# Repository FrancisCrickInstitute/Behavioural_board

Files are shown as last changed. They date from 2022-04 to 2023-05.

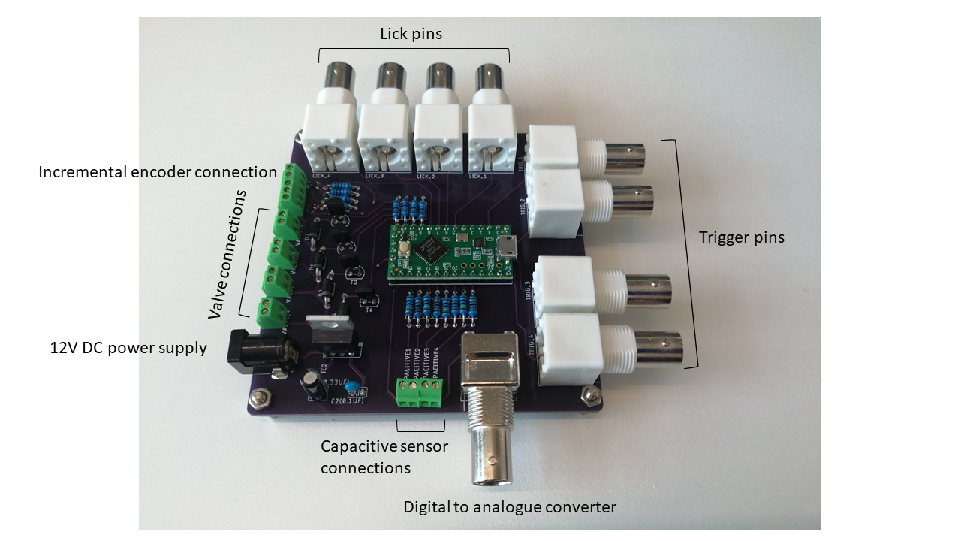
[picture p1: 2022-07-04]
Behavioural board V2.png

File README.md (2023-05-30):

# Behavioural_board

This piece of hardware is a Teensy 3.2, Teensy LC or Teensy 4 [1] breakout board with 4 valve controls and (capacitive) licking sensors and with the same amount of digital inputs/outputs (8 in total). This device pretends to be a tool for behavioural experiments which need to control up to four valves and sense 4 licking sensors. The board has eight digital pins with interrupt capability. These pins are connected to a BNC and they can be used to display digital signals or to trigger externally the valves for instance. The Teensy 3.2 performs very well on the capacitive sensor library [2] achieving sub-millisecond sampling periods while using one licking sensor at 120 MHz clock speed. All thought the licking frequency in mice is ~7 Hz, sub-millisecond resolution is required when accurate sensing of lick onset and offset is desired [3]. There is also an Incremental encoder connection for 5V Encoders with logic level shifters for phases A and B.

Behavioural board v2

# R1-R8 resistor values (Capacitive sensor pins resistors)
The value of the capacitive sensor emitter is 1MΩ and the receiver digital pin has a 1kΩ resistance value to avoid an accidental electric shock [5]. The value of the high resistance value resistor can be changed to higher values in order to increase sensitivity.

# R9-R12 Calculation example (Transistor base current)
The solenoid valve used for the design is the Lee company model LHDA0533215H. The current needed on the transistor collector has been calculated using the power and the resistance from the manufacturer specifications [4]. Different solenoid valves may require changing the transistor base resistor. More details on "R9-R12 Calculation example (Transistor base).pdf"

# Limitations

If you are using Teensy LC Pin 1 does not have interrupt capability, therefore Trigger 1 cannot be used using interrupts. The DAC BNC connector is wired with to A14 of Teensy 3.2  and A12 of LC so it cannot be used with the Teensy 4.0.

# References

[1] 	"https://www.pjrc.com/teensy/teensy31.html". 

[2] 	"https://github.com/PaulStoffregen/CapacitiveSensor". 

[3] 	B. Williams, A. Speed and B. Haider, "A novel device for real-time measurement and manipulation of licking behavior in head-fixed mice," Journal of Neurophisiology, vol. 120, pp. 2975-2987, 2018. 

[4] 	"https://www.theleeco.com/products/electro-fluidic-systems/solenoid-valves/control-valves/lhd-series/3-port/ported/". 

[5] 	"https://www.pjrc.com/teensy/td_libs_CapacitiveSensor.html".

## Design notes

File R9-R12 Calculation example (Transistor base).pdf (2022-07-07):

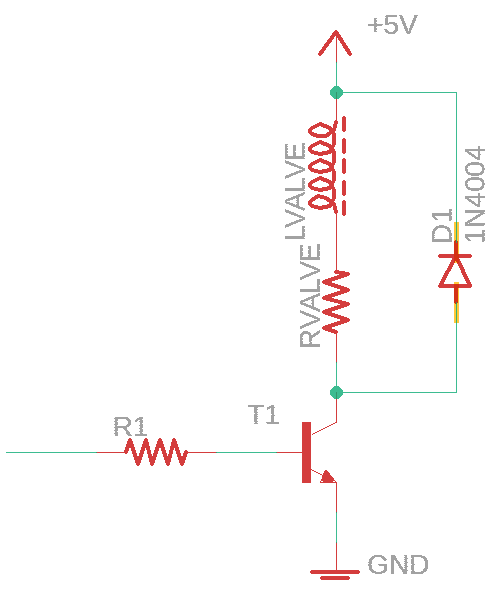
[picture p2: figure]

Pvalve = 550 mW Rvalve = 46 Ω

Pvalve = Ivalve

2
∗ Rvalve

Ivalve = √
Pvalve

Rvalve

= √
550 mW
46 Ω

Ivalve = 109 mA

BC 337 NPN Transistor

ℎFE = 100 IC = 100mA VCE(ON) = 1.2V

IB =

IC

ℎFE

=

100 mA
100 = 1mA

BE mesh

−TTL + IBR + VCE(ON) = 0

−3.3V + (1 mA)R + 1.2V = 0

R1 =

2.1V
1mA = 2.1kΩ

CE mesh

−Vcc + RvalveIC + VCE = 0

−3.3V + 46Ω 100mA + VCE = 0

VCE = 1.3V

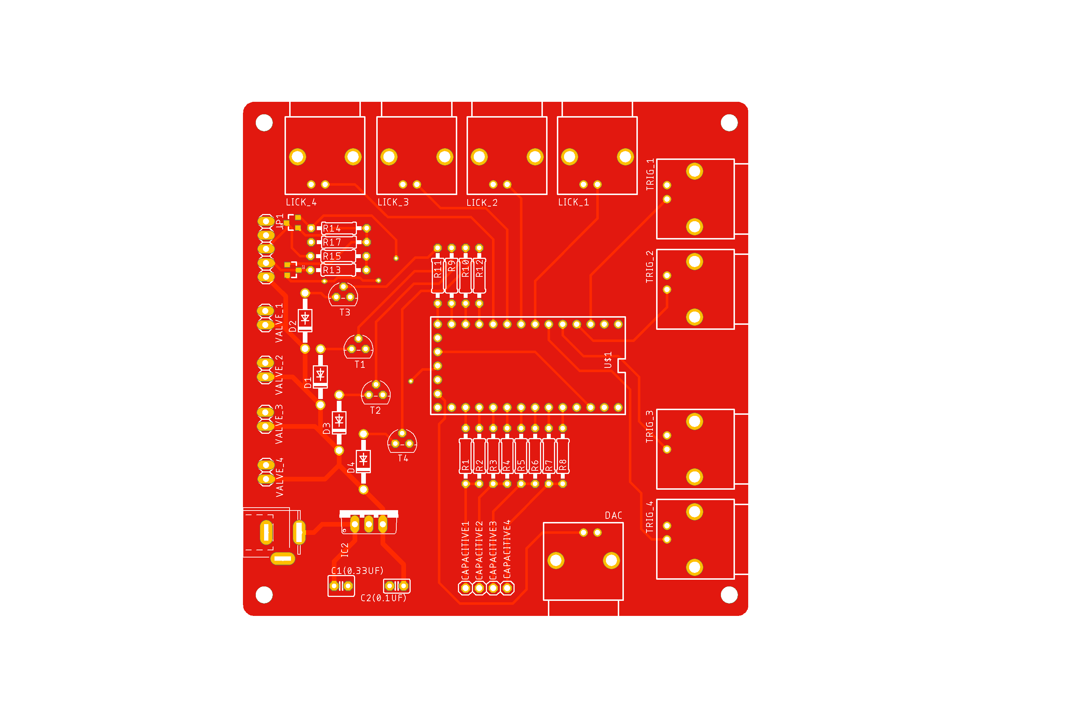
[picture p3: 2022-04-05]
Design files/Behavioural board V2.png

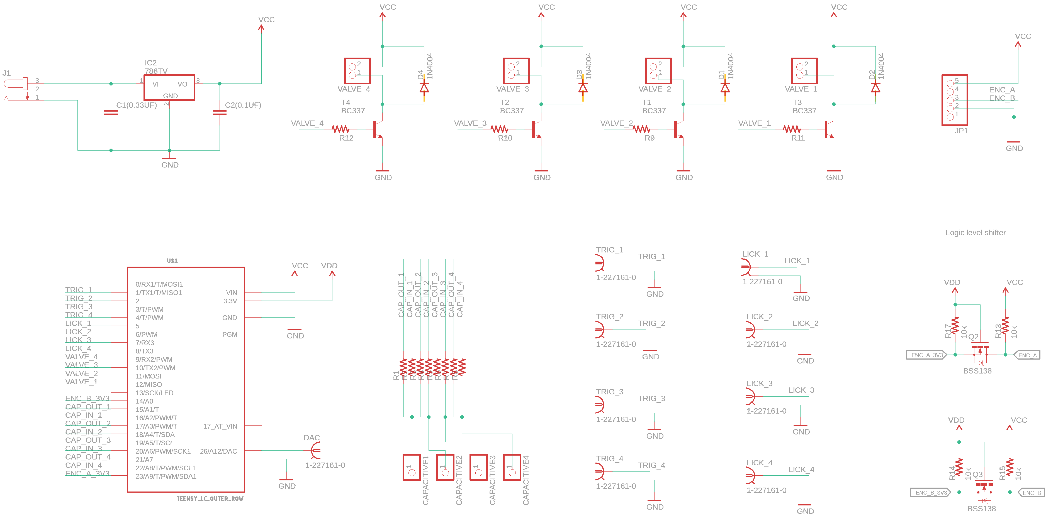
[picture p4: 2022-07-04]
Design files/Behavioural board V2 Schematic.png

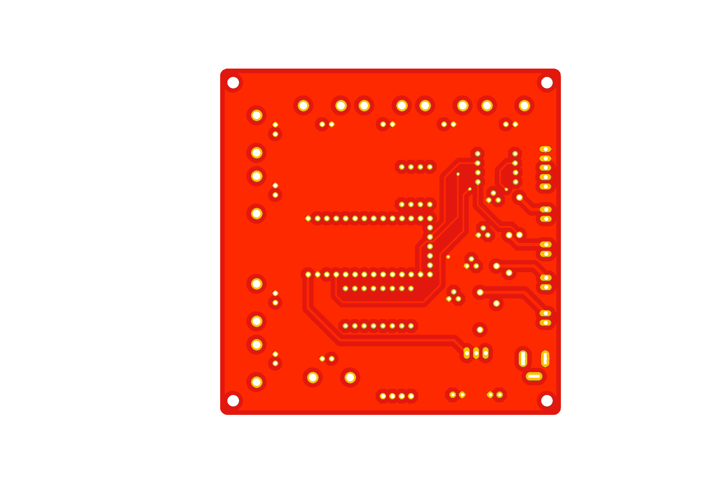
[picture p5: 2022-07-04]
Design files/Behavioural board V2 bottom.png

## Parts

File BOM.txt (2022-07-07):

Partlist exported from C:/Users/ferrerx/Documents/GitHub/Behavioural_board/Design files/Behavioural board V2.sch at 6/17/2022 1:58 PM

Qty Value               Device              Package                     Parts                                                               Description                            MF               MPN      OC_FARNELL OC_NEWARK POPULARITY SPICEPREFIX
1                       C2.5/2              C2.5-2                      C2(0.1UF)                                                           CAPACITOR                                                                             28                    
1                       C2.5/4              C2.5-4                      C1(0.33UF)                                                          CAPACITOR                                                                             6                     
1                       JACK-PLUG0          SPC4077                     J1                                                                  DC POWER JACK                                                    unknown    unknown   0                     
4                       PINHD-1X1           1X01                        CAPACITIVE1, CAPACITIVE2, CAPACITIVE3, CAPACITIVE4                  PIN HEADER                                                                            64                    
4                       PINHD-1X2           1X02                        VALVE_1, VALVE_2, VALVE_3, VALVE_4                                  PIN HEADER                                                                            98                    
1                       PINHD-1X5           1X05                        JP1                                                                 PIN HEADER                                                                            69                    
12                      R-US_0207/10        0207/10                     R1, R2, R3, R4, R5, R6, R7, R8, R9, R10, R11, R12                   RESISTOR, American symbol                                                             36         R          
9   1-227161-0          1-227161-0          AMP_227161                  DAC, LICK_1, LICK_2, LICK_3, LICK_4, TRIG_1, TRIG_2, TRIG_3, TRIG_4 JACK,  RIGHT ANGLE, 50 OHM, PCB, BNC   TYCO ELECTRONICS 1-227161 unknown    33B3200   0                     
4   10k                 R-US_0207/10        0207/10                     R13, R14, R15, R17                                                  RESISTOR, American symbol                                                             36         R          
4   1N4004              1N4004              DO41-10                     D1, D2, D3, D4                                                      DIODE                                                                                 82                    
1   786TV               786TV               TO220V                      IC2                                                                 Positive VOLTAGE REGULATOR                                                            0                     
4   BC337               BC337               TO92                        T1, T2, T3, T4                                                      NPN TRANSISTOR                                                                        2                     
2   BSS138              MOSFET-NCHANNELSMD  SOT23-3                     Q2, Q3                                                                                                                                                                          
1   TEENSY_LC_OUTER_ROW TEENSY_LC_OUTER_ROW TEENSY_3.0-3.2&LC_OUTER_ROW U$1                                                                 Teensy LC with only outer row of pins.

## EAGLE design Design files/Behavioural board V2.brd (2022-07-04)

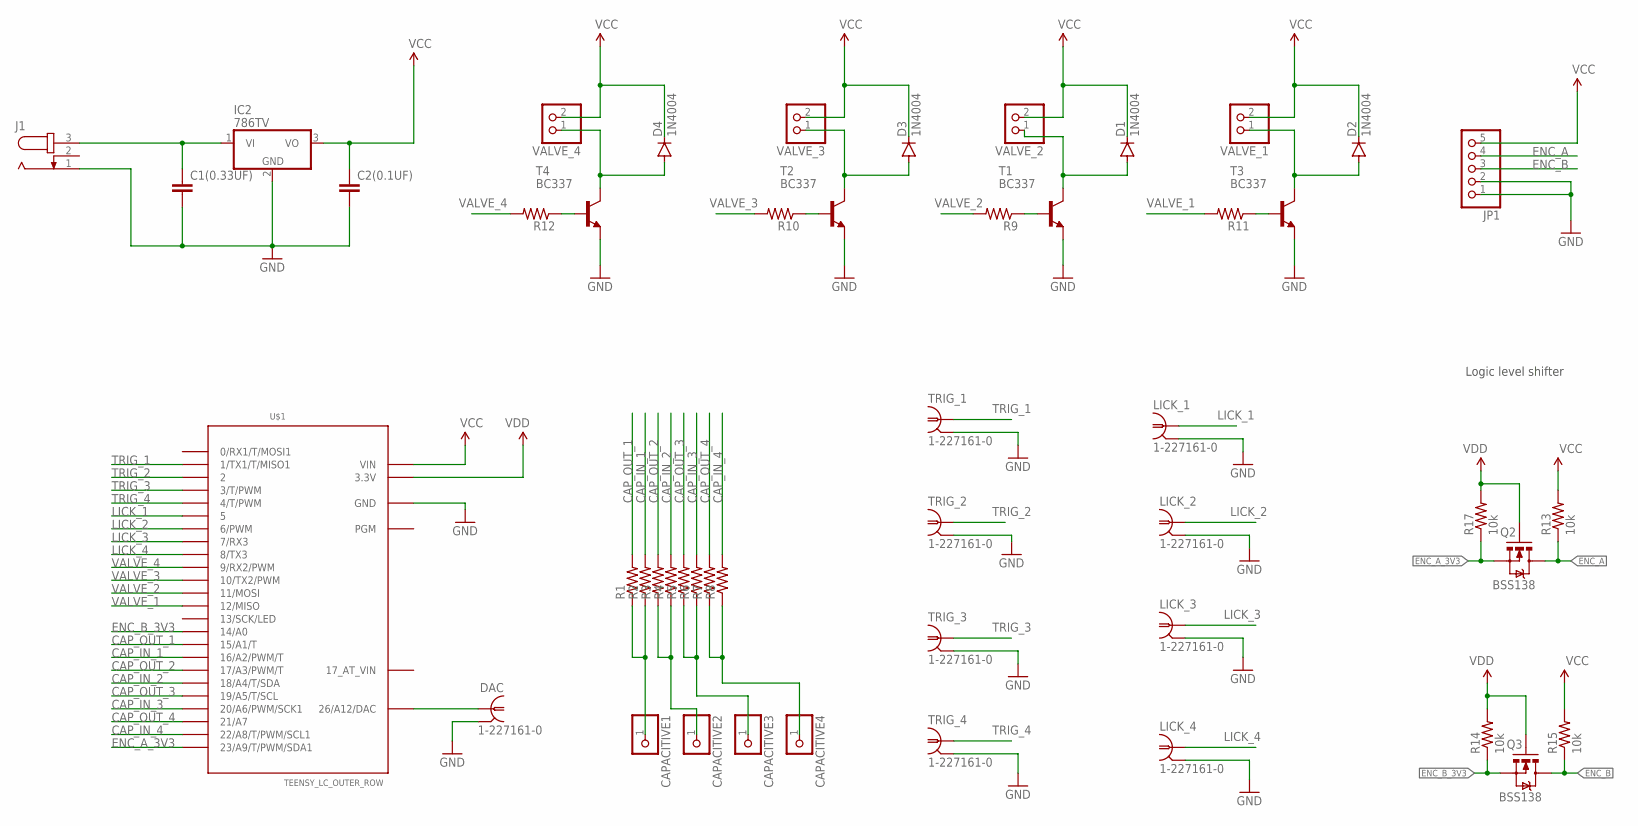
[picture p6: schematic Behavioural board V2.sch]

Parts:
C1(0.33UF): C2.5/4; C2.5-4
C2(0.1UF): C2.5/2; C2.5-2
CAPACITIVE1, CAPACITIVE2, CAPACITIVE3, CAPACITIVE4: PINHD-1X1; 1X01
D1, D2, D3, D4: 1N4004; DO41-10
DAC: 1-227161-0; AMP_227161
IC2: 786TV; TO220V
J1: JACK-PLUG0; SPC4077
JP1: PINHD-1X5; 1X05
LICK_1, LICK_2, LICK_3, LICK_4: 1-227161-0; AMP_227161
Q2, Q3: BSS138; SOT23-3
R1, R2, R3, R4, R5, R6, R7, R8, R9, R10, R11, R12: R-US_0207/10; 0207/10
R13, R14, R15, R17: 10k; 0207/10
T1, T2, T3, T4: BC337; TO92
TRIG_1, TRIG_2, TRIG_3, TRIG_4: 1-227161-0; AMP_227161
U$1: TEENSY_LC_OUTER_ROW; TEENSY_3.0-3.2&LC_OUTER_ROW
VALVE_1, VALVE_2, VALVE_3, VALVE_4: PINHD-1X2; 1X02

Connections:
12V: C1(0.33UF).1, IC2.1 (VI), J1.3
CAP_IN_1: R2.2, U$1.16/A2 (16/A2/PWM/T)
CAP_IN_2: R4.2, U$1.18/A4 (18/A4/T/SDA)
CAP_IN_3: R6.2, U$1.20/A6 (20/A6/PWM/SCK1)
CAP_IN_4: R8.2, U$1.22/A8 (22/A8/T/PWM/SCL1)
CAP_OUT_1: R1.2, U$1.15/A1 (15/A1/T)
CAP_OUT_2: R3.2, U$1.17/A3 (17/A3/PWM/T)
CAP_OUT_3: R5.2, U$1.19/A5 (19/A5/T/SCL)
CAP_OUT_4: R7.2, U$1.21/A7
ENC_A: JP1.4, Q2.3 (D), R13.1
ENC_A_3V3: Q2.2 (S), R17.1, U$1.23/A9 (23/A9/T/PWM/SDA1)
ENC_B: JP1.3, Q3.3 (D), R15.1
ENC_B_3V3: Q3.2 (S), R14.1, U$1.14/A0
GND: C1(0.33UF).2, C2(0.1UF).2, DAC.2, IC2.2 (GND), J1.1, JP1.1, JP1.2, LICK_1.2, LICK_2.2, LICK_3.2, LICK_4.2, T1.1 (E), T2.1 (E), T3.1 (E), T4.1 (E), TRIG_1.2, TRIG_2.2, TRIG_3.2, TRIG_4.2, U$1.AGND (GND), U$1.GND, U$1.GND1 (GND)
LICK_1: LICK_1.1, U$1.5
LICK_2: LICK_2.1, U$1.6 (6/PWM)
LICK_3: LICK_3.1, U$1.7 (7/RX3)
LICK_4: LICK_4.1, U$1.8 (8/TX3)
unnamed: DAC.1, U$1.RESET/DAC (26/A12/DAC)
unnamed: CAPACITIVE1.1, R1.1, R2.1
unnamed: CAPACITIVE2.1, R3.1, R4.1
unnamed: CAPACITIVE3.1, R5.1, R6.1
unnamed: CAPACITIVE4.1, R7.1, R8.1
unnamed: R11.1, T3.2 (B)
unnamed: D2.A, T3.3 (C), VALVE_1.1
unnamed: R9.1, T1.2 (B)
unnamed: D1.A, T1.3 (C), VALVE_2.1
unnamed: R10.1, T2.2 (B)
unnamed: D3.A, T2.3 (C), VALVE_3.1
unnamed: R12.1, T4.2 (B)
unnamed: D4.A, T4.3 (C), VALVE_4.1
TRIG_1: TRIG_1.1, U$1.1 (1/TX1/T/MISO1)
TRIG_2: TRIG_2.1, U$1.2
TRIG_3: TRIG_3.1, U$1.3 (3/T/PWM)
TRIG_4: TRIG_4.1, U$1.4 (4/T/PWM)
VALVE_1: R11.2, U$1.12 (12/MISO)
VALVE_2: R9.2, U$1.11 (11/MOSI)
VALVE_3: R10.2, U$1.10 (10/TX2/PWM)
VALVE_4: R12.2, U$1.9 (9/RX2/PWM)
VCC: C2(0.1UF).1, D1.C, D2.C, D3.C, D4.C, IC2.3 (VO), JP1.5, R13.2, R15.2, U$1.VIN, VALVE_1.2, VALVE_2.2, VALVE_3.2, VALVE_4.2
VDD: Q2.1 (G), Q3.1 (G), R14.2, R17.2, U$1.3.3V, U$1.3.3V1 (3.3V)

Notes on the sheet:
Logic level shifter

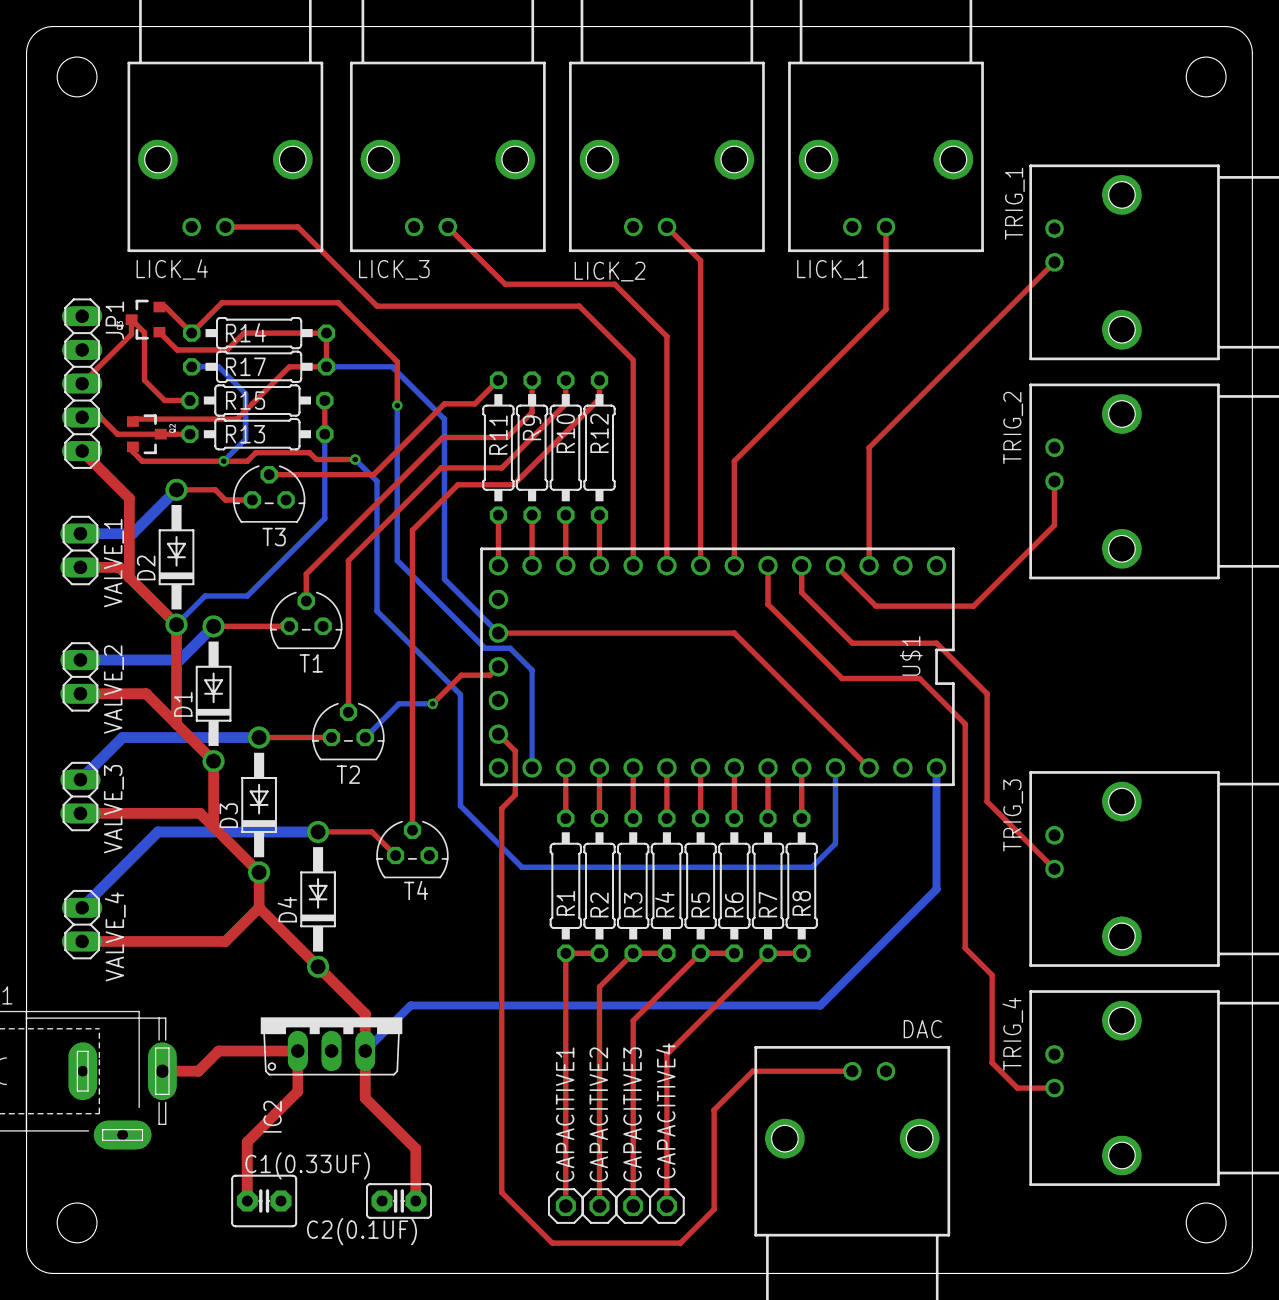
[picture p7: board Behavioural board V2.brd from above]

Board: 2 copper layers, 92.4 x 94.0 mm, 49 parts (0 on the bottom side), 41 nets.

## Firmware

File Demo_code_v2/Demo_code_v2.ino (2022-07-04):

#include <CapacitiveSensor.h>

byte N = 20;

//Capacitive sensor objects
CapacitiveSensor   CS_1 = CapacitiveSensor(15,16);
CapacitiveSensor   CS_2 = CapacitiveSensor(17,18);
CapacitiveSensor   CS_3 = CapacitiveSensor(19,20);
CapacitiveSensor   CS_4 = CapacitiveSensor(21,22);

// Licking sensor variables
long lick_1;
long lick_2;
long lick_3;
long lick_4;

//Valve variables
int valve_1 = 12;
int valve_2 = 11;
int valve_3 = 10;
int valve_4 = 9;

//Input/output pins

int trig_1 = 1; //IO_pin_1
int trig_2 = 2; //IO_pin_2
int trig_3 = 3; //IO_pin_3
int trig_4 = 4; //IO_pin_4
int lick_1_out = 5; //IO_pin_5
int lick_2_out = 6; //IO_pin_6
int lick_3_out = 7; //IO_pin_7
int lick_4_out = 8; //IO_pin_8

volatile bool state = LOW;
volatile bool state_2 = LOW;
volatile bool state_3 = LOW;
volatile bool state_4 = LOW;

elapsedMillis outputTimer = 0;

int th = 5000;

//Encoder encoder(23,14); // mistake connecting encoder to pin 13 (it has the LED attached)

void setup() 
{
  CS_1.set_CS_AutocaL_Millis(0xFFFFFFFF);
  CS_2.set_CS_AutocaL_Millis(0xFFFFFFFF);
  CS_3.set_CS_AutocaL_Millis(0xFFFFFFFF);
  CS_4.set_CS_AutocaL_Millis(0xFFFFFFFF);

  //Pins to be externally triggered
  //pinMode(trig_1, INPUT_PULLUP); // Teensy LC does not have interrupt capability on pin 1
  pinMode(trig_2, INPUT_PULLUP);
  pinMode(trig_3, INPUT_PULLUP);
  pinMode(trig_4, INPUT_PULLUP);
  
  //Interrupt routines can be used to externally trigger the valves for instance
  //attachInterrupt(digitalPinToInterrupt(trig_1),change, RISING); // Teensy LC does not have interrupt capability on pin 1
  attachInterrupt(digitalPinToInterrupt(trig_2),change_2, RISING);
  attachInterrupt(digitalPinToInterrupt(trig_3),change_3, RISING);
  attachInterrupt(digitalPinToInterrupt(trig_4),change_4, RISING);
  
  // Pins that can be used as a digital oputput
//  pinMode(trig_1, OUTPUT);
//  pinMode(trig_2, OUTPUT);
//  pinMode(trig_3, OUTPUT);
//  pinMode(trig_4, OUTPUT);

  //Valve pins declared as an output
  pinMode(lick_1_out, OUTPUT);
  pinMode(lick_2_out, OUTPUT);
  pinMode(lick_3_out, OUTPUT);
  pinMode(lick_4_out, OUTPUT);

  // Pins that can be used as a digital oputput
  digitalWrite(lick_1_out, LOW);
  digitalWrite(lick_2_out, LOW);
  digitalWrite(lick_3_out, LOW);
  digitalWrite(lick_4_out, LOW);

  //Valve pins declared as an output
  pinMode(valve_1, OUTPUT);
  pinMode(valve_2, OUTPUT);
  pinMode(valve_3, OUTPUT);
  pinMode(valve_4, OUTPUT);
}

void loop() 
{
  //Variable to check the performance of the loop function in us
  //long start = micros();

  //Read all the licking sensors
  lick_1 =  CS_1.capacitiveSensor(N);
  lick_2 =  CS_2.capacitiveSensor(N);
  lick_3 =  CS_3.capacitiveSensor(N);
  lick_4 =  CS_4.capacitiveSensor(N);

  // Actuate the valves, when each of the trig_ pins see a rising edge the state variable changes cand the 
  // vale state also changes
  //digitalWrite(valve_1,state);
  digitalWrite(valve_2,state_2);
  digitalWrite(valve_3,state_3);
  digitalWrite(valve_4,state_4);

  // Convert the licking signal to a digital output for a certain threshold
  if (lick_1 >= th)
    {
      digitalWrite(lick_1_out, HIGH);
    }
  else if (lick_1 < th)
    {
      digitalWrite(lick_1_out, LOW);
    }
    
  if (lick_2 >= th)
    {
      digitalWrite(lick_2_out, HIGH);
    }
  else if (lick_2 < th)
    {
      digitalWrite(lick_2_out, LOW);
    }
    
  if (lick_3 >= th)
    {
      digitalWrite(lick_3_out, HIGH);
    }
  else if (lick_3 < th)
    {
      digitalWrite(lick_3_out, LOW);
    }

  if (lick_4 >= th)
    {
      digitalWrite(lick_4_out, HIGH);
    }
  else if (lick_4 < th)
    {
      digitalWrite(lick_4_out, LOW);
    }

  
  // print position for display
  if (outputTimer > 20)  
  {
    outputTimer = 0;
    //Serial.println(state_4);
    //Serial.println(micros() - start);
  }
  

}

void change()
{
  state = !state;
}

void change_2()
{
  state_2 = !state_2;
}

void change_3()
{
  state_3 = !state_3;
}

void change_4()
{
  state_4 = !state_4;
}

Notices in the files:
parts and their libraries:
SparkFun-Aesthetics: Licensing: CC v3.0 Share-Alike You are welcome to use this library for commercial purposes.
